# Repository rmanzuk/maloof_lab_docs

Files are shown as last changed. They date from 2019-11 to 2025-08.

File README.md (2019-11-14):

# Lab Recipes

This repo stores and records the workflows for lab and field equipment

### Photogrammetry
- recipe for MicaSense RedEdge MX that formats the data for FRS161 2019.

### GIRI

### Sercon
- data reduction script for Sercon dataset
- workflow for running samples on the Sercon

### GPS
- Trimble differential correction workflow

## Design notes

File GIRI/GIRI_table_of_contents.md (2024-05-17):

# Master markdown file for GIRI
 GIRI is a bit of a Frankenstein machine with a lot of loosely kept knowledge of keeping it running.  This document is an attempt at putting it all together, including links to external files and webpages. From this table of contents, click on the section you want to read about. Sub-documents include helful links, images, and files.

- - -
## Physical Setup / Maintinence
### [Mitsui CNC surface grinder](sub_markdowns/surface_grinder.md)
### [Pneumatic peripherals](sub_markdowns/pneumatics.md)
### [Camera and lenses](sub_markdowns/camera_lenses.md)
### [Wiring / electronics with PLC](sub_markdowns/wiring_plc.md)
### [Summary of products to keep GIRI going](sub_markdowns/shopping_list.md)
- - -
## Operation code
### [MATLAB](sub_markdowns/matlab_doc.md)
### [Connected components ladder logic](sub_markdowns/ladder_logic.md)
### [C++ Capture One SDK](sub_markdowns/capture_one_sdk.md)
### [Other software](sub_markdowns/other_software.md)
- - -
## Data storage and organization
### [giristore](sub_markdowns/giristore.md)
- - -
## Operating recipes
### [Wheel balancing and truing](sub_markdowns/wheel_balancing_truing.md)
### [Dressing the chuck](sub_markdowns/chuck_dressing.md)
### [Focusing the camera](sub_markdowns/focusing_camera.md)
### [Preparing a sample for serial grinding and imaging](sub_markdowns/sample_prep.md)
### [Mounting a new sample for serial grinding and imaging](sub_markdowns/starting_sample.md)
### [Daily operations to grind and image a sample](sub_markdowns/daily_operations.md)
### [Accessing data on giristore](sub_markdowns/accessing_data.md)
- - -
## Education
### [Checklist of things to learn/know for operation](sub_markdowns/education_checklist.md)
### [Known current issues or improvements we would like to make](sub_markdowns/issues_improvements.md)
### [Troubleshooting common problems](sub_markdowns/how_to_fix_problems.md)

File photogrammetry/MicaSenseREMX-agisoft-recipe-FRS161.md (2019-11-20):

# Agisoft Metashape Workflow for MicaSense RedEdge MX---Specifically for FRS161
Bolton Howes, November 2019

**note: This workflow is modified from [this ](https://agisoft.freshdesk.com/support/solutions/articles/31000148780-micasense-rededge-mx-processing-workflow-including-reflectance-calibration-in-agisoft-metashape-pro<strong), to make DEMs and Orthomosaics from MicaSense RedEdge MX photographs**

<!---Press control+shift+m to view in markdown-preview in atom-->

## 1. Add Photos (5 minutes)
- open Workflow menu and choose Add Photos. Select all images including reflectance calibration images and click OK. Select the "Multi-camera system" option.

## 2. Locate reflectance panels
- open Tools Menu and choose Calibrate Reflectance. Press "Locate Panels" button.
- Images with the panel will be moved to another folder and the masks will be placed over the images. If the images are not automatically, see Appendix A from [this workflow](https://agisoft.freshdesk.com/support/solutions/articles/31000148780-micasense-rededge-mx-processing-workflow-including-reflectance-calibration-in-agisoft-metashape-pro<strong). You may need to load a CSV with the calibration information.

## 3. Run reflectance calibration (2 minutes)
- Check on "use reflectance panels" and "use sun sensor" option sin the Calibrate Reflectance dialog to perform calibration. Click OK to start the calibration.

## 4. Enter Ground Control Points (GCPs)
- click on the 'Reference' panel, which is in the bottom left of the Metashape window.
- Right click in the Markers on the left middle panel, and select 'Add Marker'
- Input the differentially corrected Lat/Long/Elev/Uncertainty
- Then right click on the marker you just created and select 'Filter Photos by Markers'
- In the 'Photos' panel only the images with your marker will be present. Double click on one of the images, then drag the predicted marker position to the actual position. Do this on at least 10 of the photos, more if you are feeling ambitious.
- Repeat for all of your GCPS

## 5. Convert from Lat Long to UTM
- In the Refernce panel, the fourth icon from the left is the 'Convert' button. Hover the mouse over it to make sure, then click it.
- The camera is in WGS 84 Lat Long, to convert to UTM, click on the drop down with WGS 84, then select 'more options'.
- Find the appropriate UTM Zone, for example the UTM for Mesoraca, Italy is 33S. So after selection the drop down window would say "WGS 84/UTM zone 33S (EPSG::32733)"
- Make sure both 'Cameras' and 'Markers' are checked on
- press OK

## 6. Align Photos (>5 hours for 1,000 photos. Depends somewhat on GCPs)
- Workflow --> Align Photos
- Use Accuracy: High
- Generic preselection and Reference preselection are checked on.
- Key point limit: 40,000
- Tie point limit: 4,000
- Adaptive camera model fitting OFF

## 7. Optimize Cameras (10 minutes per iteration. ~1-2 hours)
- It is easy to overdo this step. So be careful and keep an eye on the dense cloud to make sure no weird shapes start popping out.
- Go to **Tools**-->**Gradual Selection** and select **reprojection error**. Select all points above 0.5 and press **OK**.
- On your keyboard press delete (FN+Delete on Macs, Del on PC).
- Then press optimize Cameras
- repeat for 2-3 iterations.
- Then using one of the selection tools, select the tie points that that seem bad (i.e. are way above or below the rest of the model) and delete them, then re-optimize the cameras. 

## 8. Build Dense Cloud (Time: 4hrs for 1,000 photos)
The Dense Point Cloud allows us to reconstruct a more accurate DEM.
- Workflow --> Build Dense Cloud
- Quality: Ultra High
- Depth Filtering: Agressive
- Calculate point colors checked on.

**Note: if you do not use Ultra High setting, your DEM will be downsampled and at MUCH lower resolution than the orthomosaic. for example, Medium produces a 1/4 resolution DEM compared to the orthomosaic.**

## 9. Build DEM (Time: 5 min)
- Workflow --> Build DEM
- Make sure the geographic projection is correct. Should be the same as Step 5
- Set interpolation to Extrapolated
- Press Ok

## 10. Build Orthomosaic (Time: 3 hrs)
- Workflow --> Build Orthomosaic
- Default settings
**Note: the Metashape estimate will say something like 12 hours, but it finishes much faster than that**

## 11. Exporting
- right-click on DEM in the 'Workspace', select export DEM
- Choose 'Export TIFF/BIL/XYZ'
- Leave the defaults, except only select 'Write BigTIFF file' in the 'Compression' panel.
- Repeat steps with Orthomosaic

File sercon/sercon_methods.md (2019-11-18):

# Sample Prep for Analysis on the Sercon

## 1. Cut   

  Before you begin, determine which machine is best suited to your sample. The **tile saw** is used to cut fresh surfaces in hand samples. Anything larger can be cut using the **oil saw**. If your sample is porous, consider the implications of filling pore spaces with oil (which will have some Carbon signature) before using the oil saw. Wear safety glasses and ear protection for this procedure.

  ### Tile Saw

  a. Turn on the water using the yellow lever to the back-right of the saw. Ensure there is a light stream of water running over the blade before turning on the saw. **The saw floods very easily** so leave the water on for as short a time as possible.

  b. Place sample on the cutting table flattest side down. Recall that you're hoping to cut a sample thick enough to drill without breaking into fragments under pressure.

  c. With the sample not touching the blade, turn on the saw using the black switch.

  d. Slowly slide the sample through the blade, making two parallel cuts. Note that the blade is diamond tipped, meaning it will not cut your finger if you touch it, but it will cut through your nail.   

  e. Turn off the blade and the water between samples, and remove any sample fragments from the cutting table.

  #### Common Problems
  The hose at the back of the metal pan in which the saw sits will occasionally get clogged with fine silt. Use your finger to unclog the inside of the hose.

### Oil Saw

  a. With the saw turned off, and the lever in “return” position, open the top of the saw. Pull the sample stage away from the blade and place your sample on it. Ensure that the sample is tightly secured, flattest side down, and will not move when the saw is running.

  b. Once the sample is tightly secured, close the top of the saw (pull the hinge that props it open towards yourself), put the lever in “cut” position, and press start. The saw can run unattended.

  c. Once you hear that the saw has completely finished its cut, open the top of the saw and remove your sample.

  d.The sawed sample will be coated with oil. Scrub/soak it with warm soapy water to remove all oil residue before proceeding with polishing or drilling.

## 2. Polish  
Polish non-homogenous samples to distinguish between clasts and matrix while drilling

  a. Ensure samples are clearly labeled on multiple sides and that the polishing surface is completely flat. If you need to flatten your sample, use wet/dry sandpaper.

  b. Evenly spread one cup of silicon carbide over the polishing tray, and pour a thin layer of water over it.

  c. Turn on the polisher using the black switch (hanging) by the bucket of rock waste. Silicon carbide water splashes out, so don't stand too close.

  d. Draw a black line across the sample using a Sharpie, and place the samples line-side down on the polishing tray.

  e. Turn on, checking periodically, and adding silicon carbide and water as necessary. Samples are polished when the black line is gone.

  g. Clean and dry the polisher. Using paper towels, remove and dry the rubber ring in the polisher. Absorb most of the liquid remaining on the polishing table using a sponge. Hose dry any remaining liquid (using the extendable air hose over the work table). Improper drying will rust the polisher.

## 3. Drill
  Used to produce powders for running on the Sercon for C and O isotopes. Wear safety glasses for this procedure.

  a. Ensure the drill is clean and has the right-sized drill bit. The chuck is latched on the top left of the drill, and it can be used to change the drill bit.  

  b. If necessary, adjust the stage by unlocking the red turn key on the left of the drill and turning the crank on the right. Lock the turn key after adjustment.

  c. Place sample on the stage, ensuring the flat side is flush to the stage surface. If the sample is not flat, place it on red bean bags for support. Always ensure that sloping rock surfaces are sloping away from you to avoid injury.

  c. Drill a shallow hole in sample (< 1-2mm). The best places to drill are often the most homogenous areas of the sample. Note that this can vary from project to project - it may be necessary to sample from clasts, fossils, or other heterogeneities. Multiple drill holes may be required to obtain enough powder for analyses.  

  d. Ensure plastic sample vials are clearly labeled on cap and side, and use weighing paper to transfer powder into vials.

  e. Use the air hose to clean the drill bit, and drilling surface in between every sample.

  #### Common Problems

  The head of a used drill bit might break if too much pressure is applied. When this happens, the head flies off, downslope. Always ensure that sloping rock surfaces are sloping away from you.

## 4. Weighing samples
During this step, you will weigh out samples for sercon analysis. **Note that procedures for standards are highly subject to change.**

a. Locate clean sample vials on the lower shelf of the oven. Bring vials to your weighing space (to the right of drill).

b. Air hose the table and wipe down the surface with kim wipes.

c. Determine the layout of your standards and samples by following the diagram below, and clearly label the vials as such. Samples will occupy the blank spaces. Run order is right to left from the bottom to top most row.

| N 	|   	|   	|   	|   	|   	| V 	|   	|   	|   	|     	|     	|
|:-:	|:-:	|:-:	|:-:	|:-:	|:-:	|:-:	|:-:	|:-:	|:-:	|:---:	|:---:	|
| V 	|   	|   	|   	|   	|   	| V 	|   	|   	|   	|     	|     	|
| N 	|   	|   	|   	|   	|   	| V 	|   	|   	|   	|     	|     	|
| N 	|   	|   	|   	|   	|   	| V 	|   	|   	|   	|     	|     	|
| V 	|   	|   	|   	|   	|   	| V 	|   	|   	|   	|     	|     	|
| N 	|   	|   	|   	|   	|   	| V 	|   	|   	| V 	| CMT 	| CMT 	|

d. For the NBS standard, weigh out 15–20 grains using the metal scooping tool. This is a scoop and look technique, and it is quite approximate.  

e. For the VTS standard, use the black well to weigh out two (tightly packed) to three (loosely packed) "divots". If it is your first time using the VTS standard, weigh out three divots.

f. Place the well over the vial with the divot side facing down. Tap the top of the well to ensure all of the powder enters the vial.

g. For the CMT standard, weigh out one divot. Repeat step f.  

e. When weighing samples, use the black well to weigh out one to three divots. The necessary amount of powder for each sample is dependent on its carbonate content, as well as the sensitivity of the machine. Most samples require two divots, unless a test run shows otherwise.

f. Allow rack of vials to sit in oven for at least an hour to remove any moisture from the samples.

# Mass Spectrometer Analysis - Starting and Monitoring a Run

## 1. Load Acid
Wear gloves for this procedure

a. Under the hood, unwrap the para-film sealing the acid container.

b.Using a small plastic funnel, slowly pour acid into a small glass vial, filling it to the top.  

c. Cap the vial and place it in the heating block in the columns to the far right.   

## 2. Flush
a.	Remove the rack of vials from the oven. Partially screw on the caps for all tubes, using different colored caps for standards and samples. Caps should be screwed on just enough so you can pick up the vial using only the cap. It is good practice to randomly cap vials to eliminate potential for systematic isotope fractionation due to exposure to moisture in the air.

b.	Systematically go through and tighten each cap. When tightening the caps, tighten until you notice a divot forming in the septum. Then, loosen slightly until there is no divot.

c. At the He flush station, insert loose needles into the edge of the septa. Avoid puncturing the middle. Discard any bent/broken needles in the red sharps box by the flush station.

d. Insert flush needles into horizontal vials, starting at the pressure gauge, and ensuring that the flush needles only puncture the edge of the septa. The flush needles are connected in a series-circuit style. This means they should always be added to the system in sequential order (starting at the first needle) and be removed in reverse order. Following a different order could contaminate the vials with atmospheric air.

e. Any flush needles that aren’t puncturing vials should be capped with gray, circular rubber stoppers.

f. Turn on He (taller tank to the right) in the closet, using the left most knob on the regulator, and the knob on the tank. Turn pressure gauge on flush needles to approximately 80 psi.

g. Flush vials for about 8 min.

h. Leaving the He on until all vials are removed, remove vials in reverse succession.  

i. Once all the vials have been removed, turn off the He pressure gauge only - a full run requires two rounds of He flushing. The pressure gauge for the He flush needles should be turned off while putting on the next set of vials, however, the He tank can remain on during that time. If you are doing a smaller run, you may skip this step.

j. After all the vials in the run have been He flushed and disconnected from the He flush needles, the pressure gauge should be turned to 0 and both knobs on He tank should be closed.

k. Remove all loose needles from the vials before loading samples into the heating block.

## 2. Loading Samples
a.	Open Callisto1055 program.

b. Click Sample List in upper left corner, and the previous sample list will pop up.

c.	Rewrite sample list with new sample names. The program does not support decimal points, and so may suggest reviewing errors in the list, if you accept errors, it will automatically correct decimal points to underscores.The last two columns should read: Weight = 100, Set Up = CTC-8. The last row should have the sample name “END”, Weight = 0, and Set Up should be empty.

d.	Save As a new file with the format mmddyy_ABC (ABC = your initials).

e.	Load vials row by row into heating block in same order as entered into the sample list. Keep the lid on the heating block as much as possible while loading since heat is lost very quickly.

f.	Allow heating block temperature to equilibrate to 69–71°C, to avoid fractionation of oxygen isotopes during acidification. This temperature can be reached faster by insulating the heating block with foil.

## 3. Acidification
Use gloves when completing this procedure.

a. Remove two small needles from the bag of small blue needles, and a syringe from the box in the right most, under bench storage closet. Tighten the needle on the syringe to avoid leaks.

b. Prior to acidifying, use a small blue needle to puncture the edge of the septa of each vial to release pressure.

c. Remove the acid vial from the heating block after the acid has heated for at least 1-2 hours.

d.	Insert small needle into the edge of the septum on the acid vial to allow for air to flow in as acid is drawn.

e. Puncture the other edge of the septum with syringe. Holding the vial upside down, draw in acid. A full run (72 vials) needs close to two full syringes for acidification.

f.After drawing acid, return the acid vial to the block, to keep it warm (and less viscous).

g. Holding the syringe needle vertically, with a kimwipe wrapped around the top, slowly press the plunger to remove any bubbles. If bubbles remain behind, pull back the plunger to create an air pocket, and then repeat the process until no bubbles remain (in the syringe or in the green neck of the needle).

h. Starting at beginning of run, puncture the bottom left corner of the septa (see figure below), inserting enough acid to react with the sample completely. This is generally about 3 drops or half the distance between the markings on they syringe. Angle the needle towards the vial wall so that the acid flows down the side of the vial. This is crucial so that the acid warms up as it drips down the side, and reacts properly with sample. Keep count of the acidified vials.

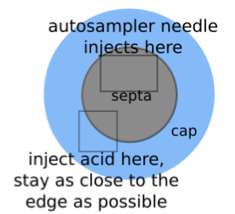
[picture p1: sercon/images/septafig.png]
septa figure


i. If there are any visible drops of acid on the septum, wipe them off with a q-tip before starting the run.

j. Start the run 1.5-2 hours after the first sample was acidified. This allows for most of the samples to dissolve completely.

#### Mixing Acid
Follow this procedure when there are multiple vials of acid in the heating block or we are running low on acid.

a. Once there are a few vials of used acid in the block, empty them into the acid container.

b. Place container on the hot plate in the hood at 150˚. Cover with a watchglass and stir with stirring rod until the mixture looks homogenous, then let it cool to room temperature.

c. Pour acid into a plastic measuring cylinder and use the hydrometer (in drawer labeled foil/tape) to measure the density. If the density is between 1.9 and 1.95, pour the acid into the container, and seal it. If not, add a small amount of phosphorous pentoxide, mix until dissolved, then cool and re-measure density.

d. When acid runs out, follow instructions taped to the hood to make a new batch of acid – wear gloves, and a lab coat while dealing with phosphoric acid and phosphorous pentoxide. Always start with ~50% phosphoric acid volumetrically, since phosphorous pentoxide will increase total volume i.e. for 100 ml of acid, start with ~50ml of  phosphoric acid.

## 4. Starting the Sercon

a. Wipe the sampling needle clean with a kimwipe. Change out the septa in the He flush valve on the left side (new septa can be found in the drawer just below the keyboard).

b. Record He, and Ref1 values from the gas bench in the lab book.

c.	Record the vacuum reading from the program (as a fraction A/S), and the reading on the He tank on the right wall of the closet.

d.	In the source control window on the right, click Load, then select “CO2.src”

e.	Turn on CO2 by clicking the CO2 tank on the mass spec diagram and wait for the mass 44, 45, and 46 (colored bars) to stabilize. Record those values.

f.	Click “peak 2”, and then “center” once the graph appears. This checks whether the magnet is centered. If the magnet is centered, there will be a green line at the center of the curve. If not, two lines, a red and a green, will appear. The green line is the center. Click “Enable” on the source control window, and use the right most single arrows to move the red line. A black line appears to show the direction in which the line is moving. Re-center if needed and save (rewrite) CO2.src if the HT value was changed. If the value was changed, re-check the center after saving the file.

g. Record HT, HP, Focus, Trap, eV, IR from the source control window.

h.	Close CO2 by clicking button on diagram again.

i.	Click “Start” (top left), and make sure it has the correct sample list name (mmddyy_ABC). Okay the file name, then source file, tick the box for stand-by, and okay the last window.

j.	The run will start, and graphs will appear in the middle window. Click “Toolbar” then “Set axes”, click save and exit, and then “Redraw” to properly scale the peaks.

k.	The first five peaks (square) are reference peaks. Record “load” and “inject” values from the flowmeter for the first non-reference (curved peak) at the start of the run.

l.	Compare all values recorded in the lab notebook to previous values. Notify the appropriate person if you notice a difference in these values.

m.	Periodically record tuning parameters in “Sercon tuning log” Excel spreadsheet on the Mac by the scopes.

## 5. Monitoring run

a. Ensure that at least the first two curved peaks look normal

b. Check sercon periodically, but it can be left alone overnight.

c. After the run has been completed, change out the septa in the He flush valve on the left side (new septa can be found in the drawer below the keyboard). Make sure the septa isn’t screwed on too tight (the septa should not be convex).

# Mass Spectrometer Analysis - Data Reduction

a. Open the Reprocessor and use the “Replay” button to find and open your file. If the Reprocessor was open, your file will not appear the first time you hit “Replay”. You will need to close the Replay window and reopen it to find your file.

b.	Go through the non-reference (curved) peaks for all samples and check that they are approximately the size of the reference peaks. Any peaks that are too low might correspond with popped caps, broken vials or undissolved sample. Peaks that are too high or too low will likely yield data with high standard deviations, and may need to be re-run.

c. Leave vials in heating block while reducing data to corroborate any anomalous values with vial order, popped caps, broken vials, etc.

d. The Sercon computer is not connected to the Internet. Save the “mmddyy_ABC.prn” file for the run onto a flash drive. The file can be found in a folder within the “Replay shortcut” folder on the desktop.

e. All data reduction is done on the Mac by the scopes. Drag and drop the .prn file into the “Raw Data” folder in Matlab.

f. Switch to the “Original_Sercon_Code” folder. Run the script “sercon.m” using the following command: sercon('mmddyy_ABC.prn',a,b) where mmddyy_ABC is the filename, a is the number of samples in the run, and b is the desired starting sample (almost always 1).

g.	A 5-subplot figure will be presented. The histogram in the lower left corner illustrates the occurrence of peak areas for each sample/standard. The peak area is the amount of gas collected for that measurement. The scatter plots (subplots 1-4) show peak area vs. raw ratio of carbon and oxygen isotopes for the standards.

h.	Select the peaks to include in the reduction. As the isotopic ratio for each peak is partly dependent on peak area, it is important to exclude any peaks that are too small or too large, since including them could produce large standard deviations.

i.	Click on the histogram to select the peak areas that will be used for data reduction, starting with the lower-bound (left) and ending with the upper-bound (right). This will need to be done twice, once for carbon isotopes and once for oxygen. It is best to exclude the tail ends of the sample peak area distribution. Ideally, there will be a Gaussian distribution of peak sizes.

j. A new 4-subplot figure will appear. The top two plots illustrate the raw carbon and oxygen values of each peak of each NBS standard, while the bottom two depict the same for the VTS standards.

k. Matlab will give the prompt “Exclude any NBS?”
Exclude any NBS standard that does not fit a line of best fit with the other standards, either with regard to carbon or oxygen isotopes.  

l. Matlab will then give the prompt “Exclude any VTS?” Repeat step k for VTS.

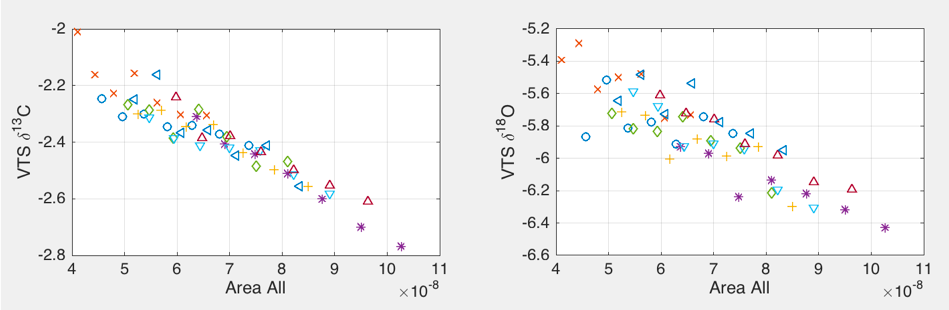
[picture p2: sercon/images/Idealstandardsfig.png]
ideal standards figure

Ideal configuration of standards, where all standards follow a tight, linearly decreasing trend  

not standards figure
Highly variable standards, which indicate a problem with the sercon or sample loading

#### Common Problems - Steps j-l

a. The machine is tuned to optimize accuracy over a certain range of peak sizes. If the peak area is way too small or way too large relative to the reference peaks, it can be out of range for how the machine is tuned and won’t produce accurate data. If the sample just prior to a standard has a peak size that is way too large, it can overload the collector and influence the results.

b. If the sample was not acidified completely or acidified at the incorrect temperature, it might have fractionated away from the standard’s reported value.

c. If a cap pops off, the seal is broken and atmospheric air flows in. The CO2 gas produced from the reaction of acid and sample may leak out and the machine then measures air. Because air has much less carbon than CaCO3, the peak size will be extremely small. This is probably the most common error.

d. If the needle or tubing is clogged with septa or acid then not all of the gas will reach the collector.

e. If a flush needle is leaking, then atmospheric air will still be in your vial and it won’t have completely flushed with He, meaning it will slightly change the overall measurement.

ideal peaks figure
Proper sized sample peaks

## Data Reduction Continued

m. 4 new figures will pop up. They are stacked, so move the figures apart to see all of them. Figure 1 shows all of the standards included in the reduction. Use this graph to answer the prompt: “Which is the primary standard?” This will be the standard that the data is corrected to in the case of a single point correction. Use the standard with the most data points as the primary standard, as it will be more statistically robust.

n. Figure 2 shows those standards if they were to be adjusted using the linearity defined by the NBS standard slope. Essentially, Matlab is determining the slope of the line of best fit through the NBS data and rotating it to horizontal. It then translates this line up or down to pin it to the known value of the standard, and then makes this correction for all NBS data (top two graphs) and all VTS data (bottom two graphs). This is a way to correct our data so that the isotope values are no longer biased towards peak area. Figure 3 shows the same thing but using the VTS slope. Figure 4 uses a slope that is the average of the NBS and VTS slope.  

o. Determine which slope best represents your data. The slope correction that minimizes standard deviations for carbon and oxygen will be the most accurate correction. Sigma values should be 0.1 or lower for carbon and 0.25 or lower for oxygen.

p. Matlab will give the prompt: “Which slope should we use?” Enter N, V, or mu (mu = μ = average) depending on which slope is most accurate to reduce data with.

q. You will be presented with a final figure containing two subplots. The knick point in each plot (y = 0) is the known value for the primary standard.

r.	Use the graph to estimate the difference between TP and SP for the secondary standard. Do this by first locating the value of your secondary standard on the x axis. Then, see where this x value intersects the plot. Ideally, the y value (difference) should be < 0.1 for d13C and < 0.25 for d18O, which indicates that the standards are in agreement. In this scenario, it is best to reduce the data using a TP correction. If the difference is much greater than this range, it is best to make a SP correction. Enter TP or SP for prompt “Two-point or Single-point correction?”

Note: If you are unsure about which correction to use, try reducing the data twice, once with each type of correction. Use whichever method produces the most consistent standard values, or rerun if neither creates reliable standards.

s. Final dataset will be produced. Several files recording all of the selections you made are saved. Open and examine the file "reduced_mmddyy_ABC.csv" in excel (open outside MATLAB).

t. Standards are expected to have the following values:

VTS: -1.48 ± 0.1 for d13C and -8.54 ± 0.25 for d18O

NBS: 1.95 ± 0.1 for d13C and -2.20  ± 0.25 for d18O

u.	Investigate any anomalous data points, by cross-referencing peak shape/size on the Reprocessor software. Consider rerunning samples if standards do not fit constraints or if there appears to be drift in standard values throughout the course of the run.

v.	Record standard values and data reduction parameters in “Standards” Excel spreadsheet.

# Common Problems

## Popped cap
Some of the vials have faulty threads that are incompatible with the caps, which can lead to caps “popping off” in the heating block as the plastic heats up and expands.

#### Symptoms:
This is easily identified using the Callisto Reprocessor software. The peaks for these samples will be completely flat lined, except for perhaps a small first peak.

popped cap figure
Diagnostic peak shape of a popped cap

#### Solution:
Identify vial in heating block and check to see if cap is crooked or loosely sitting on the vial. Remove the vial, wash out the acid with DI and put the vial in the broken glass box by the sink. Sometimes, the caps may be faulty. In that case, use those caps for acid vials and not for samples or standards.

Samples without any carbonate content or caps that are not screwed on completely can also give the same diagnostic signal in Callisto Reprocessor. Ensure this is not the case before throwing out a good vial.

## Clogs

Clogs can cause a spectrum of problems for the Sercon. Minor clogs, caused by pieces of septa or a thin meniscus of acid blocking part of the needle, are usually resolved on their own when the acid is pushed through to the trap. Clogs in the needle can be easily cleaned out. Acid clogs can create serious issues for the Sercon if they make it to the gas bench. This requires a lot a work to locate and clean out the acid, which blocks gas flow and corrodes parts of the machine.

#### Symptoms:
Clogs create variable data, as isotopic fractionation occurs when CO2 is not allowed to flow freely through the capillaries. Clogs are identified by irregular peak sizes and sporadic measurements from the flow meter. Take care to inject vials properly during acidification; improper acidification technique is the leading cause of clogs.

clog peak figure
Irregular peak size indicative of a clog

clog figure
Chronic clogs can also be identified during the data reduction process. Figure depicts distinct groupings of standards, which also show a gradual increase in value over the course of the run.
#### Solutions:

Contact the Lab Manager

## Unmixed acid

Always acidify using a vial of fresh acid. Combining the remaining acid from previous vials without proper heating and mixing can create variable data (see figure below).

unmixed acid figure
Highly variable standards coincident with recycling remaining acid from previous runs

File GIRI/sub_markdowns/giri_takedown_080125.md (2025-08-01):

## First, we removed the camera and its wiring. 
1. Remove camera curtain, which is velcro-ed on top around camera housing. 
2. Remove ethernet, which is a blue cord wired though the top of the camera housing. 
3. Remove the camera back: Push button on RH side, pull up to get the back out. Black square plate goes on the top of the non-viewer side. Remove batteries and put them into the appropriate slit in the foam in the large black case. We packed this into the black zippered case and into the large black box, inside the foam. The 72 mm lens, back, and batteries are all inside the white foam piece.
4. Loosen the yellow levers on the front (facing you) of the grinder to lower the ringlight. The use Allen keys (red and yellow cases) to remove the camera itself. It was set in the track, rotated so that the notches matched. The two screws are on the LH, RH sides of where the camera sits. Pictures 3908 and 9000 on PMH phone.
5. We packaged the IQ4, 72mm lens, 120 mm lens, and charger in the black box thus labeled. 

## Next, we removed the light bricks and ring light.
1. Lights 7, 8 (7 is the one closest to you when facing grinder) are the yellow cords that we unscrewed from these bricks. Pictures ...1455 and ...8445 on PMH phone. 
2. Use Allen key to remove the UV bricks by the silver arms. We taped the 2 screws along the top rim into place.
3. Took wood glass filter out (pop out 3d printed side guard, slide out) and cleaned with lens wipe. Both filters are in the same box. 
4. Unscrew ring light cords, which are labeled as L, R when you are facing grinder. Picture ..1592 on PMH phone. At this point, all cords to camera and lights are disconnected.
5. Use Allen key to unscrew ring light's connector on the right (when facing grinder). There are 3 screws; we did the closest one first. Hold up the ringlight while unscrewing. Picture ...3612 on PMH phone.

We left the rest of the camera apparatus on the grinder. 

## We then removed the roller and other connected devices.
1. On the grinder console, Func. 1 and OUT1 to move roller up and down. IMG_8892 on ACM phone. 
2. When it is up, unscrew rightmost screw on yellow 3d printed piece using Allen key, then slide off blue piece laying on top of the rim. 
3. The oil coolant unit (autolubricator) is the b/w box on the RH side of grinder. Fill it with oil from the red oil container near the coolant box. Picture 2577 on PMH phone. 

Note: The extra active wheel is 320 grit. The one currently on grinder is 400 grit. 

## PLC takedown. 
1. Grinder connection is thick yellow cord. Goes into RH side of PLC when facing PLC front. 
2. Disconnected the air--took off its yellow cord, which is in the back right when facing PLC front. 
3. Turn off grinder by flipping switch on front of grinder. 
4. Unplug black cord, which is power for the PLC.
5. Unplug gray/white PLC data to computer cord. 

## Coolant tank. 
1. Take off covers and top. 
2. Screw out the filter (hoses in front). 
3. Clean out tank and replace filter paper as needed.

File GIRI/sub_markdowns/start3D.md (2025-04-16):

### For 3D grinding + imaging
*If you are not already comfortable with positioning the grinder for ```rasterflat``` and/or setting positions and working in grinder coordinates, I suggest you practice rasterflat **first** (this will be useful for getting your sample ready to grind, anyway...)*  

Make sure the camera is on and the lens cap is off. Check coolant levels (>6") and refill. LOAD a previously used grinding code. For example, `20250416.JKW.G001.focus` adapts the old code to move the sample into the focal plane before taking images (and out of the focal plane when the imaging is done). If the camera focus is not at the bottom of the wheel, use a .focus script).  

Before grinding, we need to set X0, Y0, and Z0 (in relative coordinates). 

Z0 should be -1.00000 in MACH coordinates. This is our imaging position.  
Y0 should be at the highest point of the sample, find this carefully!  
X0 should be at the edge of the rock closest to you. The table will move *out* towards you in X as it grinds.  

In the GCODE, also set the X depth like in rasterflat.  

LTEACH and RTEACH tell the table how far to move in Z. Set these to the outer Z limits of your sample, with some (~0.5-1") room to spare.  

Enter the number of loops (L) in the usual place at the top of the code.  

Before engaging the magnet, make sure your sample is nicely centered under the lens **when the table is at Zmach = -1.00000**. Check this by opening live view in captureOne and turning on a light in matlab (serial_command('LIGHTS_000010000') turns on green). **The camera is fixed in X, so do not worry about the X position.** The only X pos in the code is where you want the grinding to start on the sample (edge closest to you).  

Once all the positions are set to 0 as detailed above, START the program, then go to the computer and, in Matlab, run ```barebones_serial```. If you have not already, create a New Session (cmd+N) in CaptureOne in the /GIRI/Data/ directory. When barebones_serial asks "which folder are the ... found in", select this newly-made folder. When barebones_serial asks how many grinds to expect, enter the number of loops you saved in your code.

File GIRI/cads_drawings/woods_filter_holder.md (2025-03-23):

# Placeholder

Asked Dave for Wood's glass filter frame design on 3/23/25.

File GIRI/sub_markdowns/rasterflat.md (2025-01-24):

# A COMPLETE GUIDE TO FLATTENING SAMPLES
## 0. Preparing your samples.
Are your samples...  
- [ ] Glued?
- [ ] Documented in the notebook?  
    page: ____  
- [ ] Photographed on the Nikon?    
    photo number: ______  
- [ ] Polished on in the lapidary so that they are mostly flat?

**If all four of these steps are complete, you are ready to get the grinder set up.**

## 1. Pre-grinding preparation.
**Polish**  
- [ ] Polish steel plates:
    - Apply a drop of **sharpening stone oil** (white cap) to the steel.
    - Using the **red stone**, polish in a figure 8 pattern until the stone passes smoothly over the steel.
    - Apply a few drops of 3-in-1 oil to the steel. 
    - Finish polishing with 10 figure-8s of the gray stone.
- [ ] Polish the chuck with the tan stone and 3-in-1 oil. Leave oil on the chuck.
**Check oil and coolant levels**  
- [ ] Check coolant levels. If less than 6", mix more coolant (see section 1.a. below.)
    -[ ] (Add coolant if needed)
- [ ] Expose new filter paper (on the roll)
- [ ] Check the back of the machine to see if leaked oil is close to filling up the overflow tub.  
    - If it is, pour waste oil into the waste container  
- [ ] Check lubricant levels on the front of the grinder. Refill with **Mobil Vactra** (blue container, in the cabinet).
**Turn the grinder/wheel on**
- [ ] Put safety glasses on (look around all 3 rooms in the lab if you cannot find any)
- [ ] Turn on the wheel (button on the computer screen) and let it run for 10 minutes if it has not run yet today.
- [ ] Turn on the coolant (button on the computer screen)
- [ ] Use the pipette to take up some coolant and make a refractrometry reading. Record this in the grinder notebook.
- [ ] Turn off the coolant.
- [ ] Turn off the wheel if it has been on for more than 10 minutes. (Fine to leave it on, too, it just might get in the way.)
      
**Sample placement**  
When flattening, you are trying to minimize time spent flattening while maximizing the number of samples that are flattened to the same heigh. So, select bars with samples that are already very close to the same height. If you don't have any, that's ok, you can flatten (and image) one bar at a time. Better to do that than spend hours needlessly grinding some bars way more than they have to be to get flat.   
Note: One of the UV brick lights gets in the way of the table, so the table **can only move so far in the Z (horizontal L/R) direction!!**  
**Z-limits (in MACH coordinates): 0.5" to 13"!**  
- [ ] Put a little 3-in-1 oil on bars and grinder chuck. 
- [ ] Place bars on chuck **ensuring that the table will not hit the UV light!!**
- [ ] Engage magnet.
You are now ready to set up your grind.

## 2. Setting up a rasterflat run.
We will always *raster* flatten our samples. It is better for the wheel and leads to a nicer finish. This means we take make one pass over the whole grinding area, then move the table up one step and do it all again. It takes a while, which is why it is imperative that your samples are mostly flat and mostly the same height before you begin.  

#### A. Measure your grinding area.  
FIRST: Move the table in the Y direction (vertical) so that there is at least an inch of space between the bottom of the wheel and your tallest sample. This ensures you do not accidentally damage the wheel.  

##### i. R and L TEACH
As the rasterflat code proceeds, the grinder will move the table in the Z direction (north-south) between two points called **L TEACH** and **R TEACH**. As the name implies, we have to "teach" these positions to the computer. Do this by moving the table so that the wheel is over the farthest left (north) edge of your samples + 0.5". At its maximum extent, this should be Z=0.5 in MACH (machine) coordinates. Press **L TEACH** on the right side of the control computer screen.   

Now, move the table so that the farthest right (south) side of your samples has cleared the wheel. At its maximum extent, this should be Z=13 in MACH coordinates. Press **R TEACH**.

To test, you can **START** the table. The table should move back and forth between the L TEACH and R TEACH points you set. Stop the table.  
##### ii. X dimension
Next, we have to figure out how wide the grinding area is (X direction or east-west). We will record this parameter in the G-code as ```X```. To do this:
1. Move the table in X so that the wheel is closer to you than all of your samples, with only a half-wheel overlap of the closest sample. (furthest west). Write down the X position in MACH coordinates:  
X0 = ____  
2. "Zero" the position so that we can come back to this X position later. (Press POS, ALL, 0 SET). All REL positions should now be zero.
3. Move the table so that the wheel is farther away from you (+half-wheel thickness) than all of your samples. Again, record the X position in MACH coordinates:  
X1 = ____  
4. The difference between X1 and X0 is the ```X``` value we will record in the G-code line that reads:
   ```G91G01X6.5F150```
You can go ahead and edit that line now to whatever you calculated. Round to one decimal point.

##### iii. Y start
You want the grind to start as close as possible to the tallest part of your sample. So, move the table well away from the wheel and lay a ruler or other flat object on top of your samples to figure out where that spot is. Once you have a since for the tallest region:  
1. Turn the wheel and coolant on (press the buttons on the control computer screen) and make sure you are wearing safety glasses.
2. Move the table so that the tallest area of your samples is close to underneath the wheel.
3. Move the table up (Y dial) *sloooowwwwlllyyyy* just until you hear the wheel barely graze the top of your sample. You should use the ```x1``` movement increment (0.0001") when you get close to the wheel.
4. Back off one or two clicks.
5. To check that you really did find the tallest spot, slowly move the table around in the horizontal (X-Z) plane to make sure the wheel doesn't touch anywhere else. If you were right, great. If not, re-calibrate with whatever new tallest area you found. Moving slowly ensures you do not damage the wheel.  

At this point, the Y position (in all coordinates) should be close to where we want to start the grind. However, ```rasterflat``` *starts* by raising the table 0.001". To account for this, we should start with Y backed-off at least 0.001" from the tallest point you found.  

6. Switch to the ```x10``` movement increment (0.001") and move Y 1 click *more positive** (table down). At this point, you will not touch the Y dial again.

##### iv. Move to the starting position
The program does not "get" any positional information from the grinder -- we must start the program from the position we want it to begin grinding at. To accomplish this,   
1. Move the table in X until X = 0.00000 in REL coordinates (you set this point before).
2. Move the table in Z until the Z value is close to your L TEACH value (this is recorded on the computer screen).
3. (Y should not have moved since you set the table height in the step iii!)

#### 2. Record your parameters and edit the G-code.
There are some important parameters that we have to record -- in the grinder notebook and in the grinder's G-code -- before we can begin.
### PARAMETERS.
Fill these out at the start of each "run" (each time you re-start the program rasterflat.txt!) We will document the parameters used for each run in the Grinder Notebook (which lives in the grinder computer room). 

#### Check and adjust these parameters in the G-code:
- ```L##```, where ## is a number (e.g. 50) that tells the grinder how many times to **L**oop (i.e. how many times to raster over the grinding area). **Do not set L>200**. If L is too large, we risk grinding away all of the rock. Let's avoid that.
- ```X#.#```, this is the difference (X1-X0) you calculated in step ii.4.
- ```F###```, the **feed rate** determines how fast the table moves under the wheel. **150** is a good starting point. If the samples are very hard (e.g. they contain a lot of chert or iron), a slower feed rate (100?) might be better. In general, do not change this if it is already set to 150.
- ```Y-0.001```, *just check* that the Y increment is set to -0.001. This is how far we will step the table up (closer to the wheel) each raster.
  
**IF YOU DO NOT KNOW WHERE THESE PARAMETERS EXIST IN THE ```rasterflat``` CODE, CHECK THE EXAMPLE CODE (```20250121.demo.rasterflat.txt```) AND ASK JULIA/ADAM.** Note that you can always demo your code by moving the table in Y so that it is very far away from the wheel and running one loop (L1) to see how the table moves. **But, it is better to just ask questions!!**

After checking/adjusting these four parameters, you can save the G-code file. Do not overwrite the ```20250121.demo.rasterflat.txt``` file. Instead, rename your file in the format:  
```YYYYMMDD.INITIALS.FXXXX.rasterflat.txt```  
```YYYYMMDD```: today's date.  
```INITIALS```: your initials.
```FXXXX```: the "**F**lattening group" you are about to grind flat.  
e.g. If I am going to flatten flattening group 1 (the first set of 2025 flattened bars) today, my code would be called:  
```20250123.JKW.F0001.rasterflat.txt```

#### 3. Start the code
At this point, the table should be in the position you want to start at. the X and Z REL positions should be very close to 0.0000, but REL Y will be some other number. **Reset everything to 0** before you start the run. (POS > ALL > 0 SET).  

If the table is positioned correctly, **the magnet is engaged**, you did everything on the checklist, and you have recorded your L,X,F parameters in the notebook, you are ready to press ```PROGRAM START``` (big green button).  

Stay in the room and monitor the first pass over your samples. If everything went as planned, you can leave. Sometimes it is helpful to time the first loop so that you have a sense for how long the whole run will take.

## 3. Finishing a run.
The code ends on its own and will stop the table, turn off the wheel, and turn off the coolant. So, it's okay if a run ends and you are not around to witness it. When you do come back to retreive your samples, if the samples do not look totally flat yet, restart your code (think about adjusting ```L``` depending on how much more material you want to remove) *without adjusting the final Y position*.   

If your samples are flat, you are done. Just a few more things to do:
- [ ] Record the final Y position (in MACH coordinates) in the grinder notebook. It will be something like -7.5757. (In REL coordinates, it should be 0.001 * the number of loops (L) that you ran.) The final Y MACH will help us focus this batch of samples.
      Y MACH at end: _____
- [ ] Move the table down so that the samples are far away from the wheel.
- [ ] Disengage the magnet
- [ ] Take a picture of each bar using the Nikon camera. Save the photo in the "PostGrind" folder and record the image number in the "PostGrind" .txt file. Place the imaged bars in a tray and make sure the tray is labeled appropriately.
- [ ] Mark each of the samples you flattened as "flattened" on the master spreadsheet.

### TROUBLESHOOTING
**Help! I need to stop my run!**
You can always press PROGRAM STOP to stop the execution of whatever G-code script is running. If things are really bad, you can also hit the emergency stop button (big and red). Stopping the program does not stop the table moving, so you also have to press TABLE STOP. Adjust your code, fix whatever went wrong, and re-start (or ask Adam/Julia!). (It is not bad to stop a run for any reason.)

### A. Sub-routines.
#### 1. Mixing coolant.
If coolant levels are below 6" (use the yellow measuring stick to measure), you need to add more coolant. If levels are just below 6", make one recipe (5L water). If levels are well below 6", make a double recipe (10L water).  
**COOLANT RECIPE**
1) Pour 5L of **DI water** into grey bucket.
2) Pour 125 mL of **Astrogrind** coolant (in cabinet) into plastic measuring cup (on sink).
3) Add the Astrogrind into the bucket of water.
4) Stir with the wooden paddle.
5) Once mixed, add the whole mixture to the coolant tub **through the filter paper**

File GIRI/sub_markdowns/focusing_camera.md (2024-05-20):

## Basic steps for getting camera in focus with the grinding plane

THE CAMERA AND LIGHTS SETUP NOW IS VERY HEAVY AND CAN BE DIFFICULT TO MOVE UP AND DOWN. RECOMMENDED TO HAVE TWO PEOPLE SO AT LEAST ONE PERSON ALWAYS HAS A HAND ON THE CAMERA.

1. **Prepare a sample**: You need a surface to focus on that you know is in-line and parallel with the grinding plane. This can be a piece of paper or a sample that you know is flat. Place a mounted sample in imaging position on the chuck, and then use either sample_flatten or raster_flat to get a flat surface that occupies most of the field of view.

2. **Set up for focusing**: Once your sample is flat, keep the table at the same y-position and move the z-position back to imaging position the field of view of the camera. Go to the control iMac, turn on the green light, and open live view in Capture One.

3. **Set the fine adjustment to middle positoin**: Finer focusing of the camera will be easier if you start in the middle fine adjustment setting and have as much room as possible to move in either direction. Twist the fine adjustment thumbscrew (circled in orange [here](../photos/camera_focus.jpg)) to the approximate middle of its range.

4. **Coarse adjust the camera**: Coarse adjustments are made by using an allen key to loosen the camera mount sled on the camera rail (circled in green [here](../photos/camera_focus.jpg)). ONCE LOOSENED, THE CAMERA WILL DROP IF NOT SUPPORTED, SO HANDS ON THE CAMERA. AGAIN, PREFERABLY A 2 PERSON JOB AT THIS POINT. Because your hands will be moving in and out of the live view feed, you probably cannot use the auto focus tools, so you will have to just move it to a position where it seems roughly in focus by eye. Then tighten the allen key back up.

5. **Fine adjust the camera**: Now that the camera is roughly in focus, you can use the fine adjustment thumbscrew to get the camera in focus. Prior to moving the fine adjustment, set up some focus boxes on the sample surface in the Capture One live view, so you can track focus. Then use the fine adjustment thumbscrew to move the camera (left to lower, right to raise) until you get the sample in optimal focus as judged by the focus boxes. If you cannot get it into optimal focus within the range of the fine adjustment, return the fine adjustment to the approximate middle and repeat the coarse adjustment based upon what you learned from the first attempt.

6. **Check focus on captured image**: Once you think you have the camera in focus, take a picture and check the focus manually. I also tend to capture a stack of images at ~half turn increments of the fine adjustment over the range of a full turn in either direction and select the position associated with the image I deem to have the best focus. This step is a little like subjective splitting hairs, so don't fret too much if you can't tell the difference between two images. You should just leave this step feeling confident the camera is in the best focus you can get it.

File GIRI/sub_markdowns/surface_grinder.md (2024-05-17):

## Mitsui CNC surface grinder

The basis for GIRI is a Mitsui MSF-818PC-NC CNC surface grinder.

#### Grinding wheel

For grinding samples, we use diamond abrasive surface grinding wheels from Norton. We use 6" diameter, 1/2" thick, 1-1/4" hole wheels. At the moment, we use a [320 grit wheel](https://www.mscdirect.com/product/details/90923806) for plunge grinding, which may even be too fine for this application and could be switched to a 220 or coarser grit in the future. To limit the appearance of scratch marks in 3D automated grinding and imaging work, we use a 400 grit wheel. The wheel was never listed on the MSC website, so contact Norton or MSC directly for a replacement. The part description is: 6X1/2X1-1/4 1A1 GRIND WHL ASD400-R75-B99-1/4QIA 

For balancing and truing the wheel, see the [Wheel balancing and truing](wheel_balancing_truing.md) section.

If there are ever any issues with surface quality when grinding, Norton tends to be very helpful in diagnosing the issue and sometimes recommending a different wheel if you contact them directly. Our most recent area rep was Ryan Chung. Ken from Millennium Machinery also recommended that we could reach out to Chuck Stormes at [South Bay Supply](http://www.southbayllc.com/aboutus/) for further adviece and even custom wheels.

#### Coolant

We try to keep coolant in the tank at > 6" depth at all times. When coolant is low, mix [Monroe AstroGRIND A](https://www.mscdirect.com/product/details/00267781) to 2.5% concentration with deionized water and pour into the tank through the filter paper. If you're doing a lot of grinding, the coolant should be completely replaced ~1 time per year. There is no great way to clean out the tank when replacing coolant, so just try to get as much out as you can with the crank pump, and scrape the rest out with something like a piece of cardboard. If you detach the pump wires from the tank, you can take it outside and try to open its valves to flush sediment out into the storm drain. Once the tank is empty and clean, refill with 2.5% coolant.

Every 6 months or so, it's a good idea to check the chemistry of the coolant, just in case anything wild is happening. We use [pH Test Strips](https://www.mcmaster.com/11235T62/), [Hardness Test Strips](https://www.mcmaster.com/11235T41/), and [Alkalinity Test Strips](https://www.mcmaster.com/11235T51/), and aim for readings around:
- pH: 10
- Hardness: 120 ppm
- Alkalinity: 240 ppm (Reading usually looks to be greater than 240, but that's the max listed on the container)

#### Autolubricator

Don't need to know much about the autolubricator (large wheeled module attached to the grinder through a few hoses). For maintenance, check the air filter on the front for dust every 6 months or so. If dusty, rinse clean in the sink. Check its oil levels, which should only have to be topped up to the yellow line 1x per year or so with [Red Mobil #6 Chiller Oil](https://www.grainger.com/product/4ZF38?gucid=N:N:PS:Paid:GGL:CSM-2295:4P7A1P:20501231&gad_source=1&gclid=Cj0KCQjwgJyyBhCGARIsAK8LVLPaWAsWm7SLFO9yRmcPppd6mvyLQ0vntz83gBcTBF1fW71n4ka5-i8aAgleEALw_wcB&gclsrc=aw.ds).

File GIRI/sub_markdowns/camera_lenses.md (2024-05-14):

## Camera

#### RCAM: 

The basis of our camera setup is a Digital Transitions RCAM, which is a solution for high-fidelity reprographic photography. This setup is common for libraries documenting/digitizing rare and important print works. The RCAM is basically a precision-machined metal tube that allows us to attach a medium-format digital camera back to one side, and a lenses (via lens boards and extension tubes) to the other side. 

#### Phase One IQ4 digital back: 
We upgraded to the Phase One IQ4 150 megapixel achromatic back in 2021. Prior to this sensor, we were using a Phase One IQ180 80 megapixel RGB back. This sensor gives the opportunity for high-resolution (~3.4um pixels) imaging of any lightwave in the back’s sensitivity range of ~400-1000nm. Note that the back itself has a digital shutter, so it should be complemented with lenses that have no shutter or have the shutter programmed to be constantly open. 

#### 120mm apochromatic Schneider-Kruznach Macro lens:
To achieve 1:1 macro photography, we use a 120mm Schneider-Kruznach APO-DIGITAR 5.6/120 M lens. This lens is apochromatic, meaning it is corrected for chromatic aberration in three wavelengths, and its wavelength vs. focal shift curve looks like a 3rd order polynomial ([figure](../photos/lens_info/chromatic_aberration.png)). We do have ways of assessing and correcting-for this chromatic abberation when doing multispectral imaging, see the supplemenary material of Manzuk, et al. 2022 for details ([link](https://gsapubs.figshare.com/articles/journal_contribution/Supplemental_Material_A_High-Resolution_Multispectral_Macro-Imager_for_Geology_and_Paleontology/19773532)).

Important note: the APO-DIGITAR 5.6/120 M lens no longer is in production, and we have not found a suitable replacement. THIS LENS MUST BE VERY WELL TAKEN CARE OF. The particular quality of the lens is in its focus flatness, that is, how it does not notably lose focus moving from the center to the edges of the image. We had tested a newer version of the lens, the aspheric, and found that it did not have the same focus flatness. A comparison of the two can be found in this [figure](../photos/lens_info/schneider_lens_comparisons.png).

We need extension tubes on this lens board to achieve 1:1 imaging. Specfically, between the lens board and the RCAm, we have a 30mm + a 40mm extention to give 70mm of extension. When installed, the setup should look like this [image](../photos/lens_info/lens_120mm_installed.jpeg). 

#### 72mm Schneider-Kruznach lens:

For larger field of view applications have a 72mm Schneider-Kruznach APO-DIGITAR 5.6/72 L lens. This lens is a lot less fancy, but achieves sharp images over an approximately 19 x 14cm field of view. 

This setup does not need to be installed with any extension tubes.

#### Wire grid polarizer:
Off-the-shelf, circular polarizers for photography only are effective in visible light. For broadband polarizing capability, we use a wire grid polarizer. We worked with a company Moxtek to create a custom solution that mounds to the 40.5mm filter thread of our lenses.

#### UV cut-off filter:
To avoid UV light contamination in our images, both due to any possible ambient sources, as well as when taking UV fluorescence images, we use a UV cut-off filter from Edmund Optics. The filter we use cuts-on at 390nm, and is monted on a 40.5mm filter thread ([link](https://www.edmundoptics.com/f/mounted-uv-filters/11546/)).

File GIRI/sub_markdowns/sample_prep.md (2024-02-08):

## Preparing a sample for serial grinding and imaging

1) This recipe assumes that your sample is well lithified or epoxy-injected such that it will withstand the grinding and imaging process without falling apart. For vacuum injection of epoxy into samples, contact [Wagner petrographic](http://wagnerpetrographic.com). We have had some luck mounting loose grains like ooids ourselves by 3D printing one of the boxes below and successively layering the grains in this [table top epoxy resin](https://masepoxies.com/product/table-top-epoxy?gclid=Cj0KCQjwsp6pBhCfARIsAD3GZuZvY6Mlc-rvrGY6VEFGhych-UP304RyY_hcOdk5y4VX3xdpKuVCHMcaAr-fEALw_wcB)

  * [simple box](../cads_drawings/sample_embedding_boxes/epoxy_box.stl)<!-- {"embed":"true"} -->

  * [sectioned box](../cads_drawings/sample_embedding_boxes/ooids_box.stl)<!-- {"embed":"true"} -->

2) Saw your sample down to size such the horizontal dimensions are roughly the size of the imaging field of view you plan to use. No need to grind superfluous rock, but a little extra is okay. Generally, rectangular prism shapes are easiest to work with, and certainly try to ensure that the top and bottom surface are close to parallel. If working with an oriented sample, I find it easiest to work with having the top surface be the oriented surface such that you know the orientation of your imaging plane and can do all later rotations with respect to that (just be sure the orientation mark is captured in one of the first images for record keeping).

3) With your sawed sample, you’re ready to mount it to a steel plate. We use 1/4” low-carbon steel sheets from McMaster-Carr. The most common dimensions we use are [3x3”](https://www.mcmaster.com/1388K102/), [3x6”](https://www.mcmaster.com/1388K106/), and [4x4”](https://www.mcmaster.com/1388K104/). Just pick a size such that your whole sample fits without much or any overhang. Sand the top surface of the steel plate and the bottom surface of your sample with coarse (~60 grit) sand paper so there is a rough surface for the epoxy to grab onto.

4) Rinse the sanded surfaces with water to remove grit, and blow dry with an air hose.

5) Put on gloves and extrude enough [2 ton epoxy](https://www.mcmaster.com/66215A24/) into a mixing cup to coat the whole bottom surface of your sample. 3-4 pulls of the trigger tends to be plenty for most samples. 

6) Mix the epoxy with a popsicle stick for at least 2 minutes.

7) Use the popsicle stick to apply a coat to the bottom surface of the sample and place the sample on the steel plate. I tend to then apply any extra epoxy to the corner where the sample meets the plate as extra reinforcement. 

8) Allow the epoxy to cure for at least 24 hours. (You can remove the gloves at this point).

9) Before placing the sample on the machine, de-bur and smooth the bottom surface of the steel plate by applying [sharpening stone oil](https://www.amazon.com/Norton-Abrasives-07660787940-Sharpening-Stone/dp/B000I1AVDW/ref=asc_df_B000I1AVDW/?tag=hyprod-20&linkCode=df0&hvadid=198090983914&hvpos=&hvnetw=g&hvrand=2480446956776683294&hvpone=&hvptwo=&hvqmt=&hvdev=c&hvdvcmdl=&hvlocint=&hvlocphy=9003941&hvtargid=pla-384768754761&psc=1) to the surface and polishing it with the coarse (red) sharpening stone in a figure 8 pattern. It may be tough to move the stone at first, but it should ease up as the plate gets de-burred. Once the stone glides fairly easily over the plate surface, you can switch to the fine (gray) sharpening stone to finish up with 10 or so more passes.

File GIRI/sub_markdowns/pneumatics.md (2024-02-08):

## Pneumatic peripherals
#### Camera shutter
#### Sample roller

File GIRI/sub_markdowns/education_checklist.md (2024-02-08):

## Checklist of things to learn/know for operation
- [ ] Wheel balancing
- [ ] Wheel truing and dressing
- [ ] Dusting the chuck (or other metals)
- [ ] G code
  - [ ] Writing simple G code for automated ginding/flattening protocols
  - [ ] Navigating main G code of 3D sample processing with imaging
- [ ] The basics of surface grinding
  - [ ] Manual grinding
  - [ ] Tips and tricks for achieving a good finish
- [ ] Daily Maintinence
  - [ ] Coolant
  - [ ] Machine oil
  - [ ] Compressed air systems
- [ ] Longer term Maintinence
  - [ ] Autolubricator
- [ ] Epoxy mounting samples to metal plates
- [ ] Setting up a new sample run
- [ ] RCAM operation and changing lenses
- [ ] Continuing to run a sample
- [ ] The grinder control computer
  - [ ] data storage and backup
  - [ ] GIRI’s operation code base
    - [ ] Matlab
    - [ ] C++ SDk
    - [ ] Capture One Processing Engine  
  - [ ] Capture One
- [ ] PLC
  - [ ] Basic wiring and rationale on setup
  - [ ] Writing ladder logic in Connected Components Workbench
  - [ ] Ring and brick lights

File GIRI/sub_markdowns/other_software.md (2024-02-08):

## Other software

#### Capture One
- To manually control the camera and view raw images, we use Capture One. Versions often change, best to be using the latest. See offline documentation for credentials.

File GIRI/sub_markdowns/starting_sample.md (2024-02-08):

## Mounting a new sample for serial grinding and imaging

1) Turn on machine switch on front of machine. If air is coming out of the valve on the right of the machine (loud hissing noise), place a finger over the valve. The hissing should stop. 

2) Turn on the camera. 

3) On the onboard computer, select “jog” and the “10x” handle command. Move table to the left using the z-axis wheel, such that most of the magnetic chuck is to the left of the wheel. Then select “auto” within the jog menu for the machine to recenter itself. We move the table to the left prior to auto-centering the positions because if the table is too far to the right, it may jog itself past its limit and throw an error.

4) On the onboard computer, go back to the main menu and select “G code.” Using the 10x and 1x toggles on the computer, bring the table z-axis (left and right) near -1.00000 in machine coordinates. After, make sure to deselect the 10x or 1x toggle so that the table does not move. We want the table around this position because that is where the grinder moves to image in the grinding and imaging protocols. No need to be very exact for now, this step can just help give you a rough guide for initially placing the sample.

5) If you have not yet, now is a good time to use the fine honing stone and [3-IN-ONE oil](https://www.grainger.com/product/3-IN-ONE-Machine-Oil-Multipurpose-Oil-4UJ34) to polish the chuck. Use a figure 8 pattern to move back and forth on the chuck. 5 passes each way should be enough.

6) Rub some [3-IN-ONE](https://www.grainger.com/product/3-IN-ONE-Machine-Oil-Multipurpose-Oil-4UJ34) oil on the machine chuck and on the bottom of the sample plate. Place the sample on the chuck in a position you think would be in the camera field of view, directly below the lens. Do not engage the magnet yet.

7) We now want to set the starting point in the y-axis (up and down) such that the wheel starts just above the highest point of the sample to avoid having to do hundreds of grind sequences before making contact with the sample. Then, using the 10x and 1x toggles on the computer, move the table down (y-axis) so the sample is well below the wheel. Move the table left-right, forward-back (z and x-axis) until the highest point of the sample is under the lowest point of the wheel. Then move the table up (y-axis) until there is less than a millimeter of space between the wheel and the highest point of the sample. Do so slowly and carefully, as a collision between the wheel and the sample may damage or even shatter the wheel. Once the wheel is close to the sample, bring the table z-axis back to exactly -1.00000 machine coordinates. Ensure the movement toggles are off. 

8) We use the imaging position (which is where the table currently is positioned) as the relative 0 in the G code for grinding and imaging. Set this position as the 0 now by selecting “pos” and within that menu select “all” and “0 set.” Close this menu.

9) Now we’ll make sure the sample is well-positioned in the field of view. This step requires the live feed, so if the mechanical shutter is in front of the lens, open it from the onboard computer main G code menu by selecting “FUNC1.” In that menu, under the “others” group, it is the “MAG” button.

10) On the control iMac, in Capture One (whichever version is current, shouldn’t matter), select the live view (the button that looks like a video camera). The feed should show the view from the camera. Gently slide the sample plate around on the chuck until the desired portion of the sample is within the camera’s field of view. Sometimes I turn the iMac around so I can see the feed while positioning the sample.

11) Once the sample is well-positioned, engage the magnetic chuck by flipping the lever to the right and close the shutter using the same command that you used to open it.

12) **Update this section once housing is finalized for new setup with ring light**

13) Time to set the starting position and the width of the sample in the x-axis (forward to backward when looking at the machine). Move the table in the x-axis until the wheel is just in front of the front edge of the sample (when standing at the front of the machine where x-axis movements are forward-backward). Sometimes it is easiest to verify this position standing near the onboard computer, looking down the z-axis. It is best to leave a few millimeters of space just to be sure the entire sample will be ground. This position is where the wheel will start a grind before moving across the sample, so extra space in this direction just adds to the time-per-grind. Not a huge deal to have extra, but don’t go crazy. Set this position to x = 0 in relative coordinates (“pos” -> “relative” -> by x select “reset” and type in 0). 

14) Enter the sample width into the G code. You can figure out sample width by moving the table on the x-axis until the wheel is behind the back edge of the sample when standing at the front of the machine. The absolute value of x in relative coordinate space is the width of your sample. You can add a few tenths of an inch just to be safe. In this case, don’t add more than a couple of tenths because superfluous movement in this direction will add time between the sample finishing grinding and moving to the roller and imaging, increasing the risk of drying before imaging. To put the sample width into the G code, find the line that reads “G91G01X_._F150. /* Move across sample…” Your sample width in inches with one decimal place will go in the blanks after X (using G code from a previous sample, the blanks will be populated with the width of the previous sample). Move the table along the x axis back to 0 in relative coordinates. Be sure to then turn off the x10 or x1 movement toggle.

15) Save the G code file. Select save near the top of the screen. Rename the file in the format “samplename.startdate” and save it. It can help to plug a keyboard into one of the usb slots on the computer to make typing easier.

16) The final step is Left and Right teaching so the machine knows which coordinates to move between on the z-axis when passing over the sample to grind it.. To do this, move the table along the z axis until the entire sample is to the left of the lowest spot on the wheel. An extra inch or so is a good idea. When you are at a good left-most position, hit “L teach” on the screen. Then move the entire sample to the right of the lowest part of the wheel, again leaving an extra inch or so, and hit “R teach.” When this is done, move the sample back to z=-1.000 in machine coordinates (should be 0 in relative coordinates).

17) You are now ready to start grinding. You can follow the next section: ‘[Daily operations to grind and image a sample](daily_operations.md)’ to get going.

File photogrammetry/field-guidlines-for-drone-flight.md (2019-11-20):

# Guidelines and Helpful Info for Flying the Drone

### Before leaving princeton

### GCPs
- bring or purchase blue tarps from a hardware stores
- if you don't have enough space for tarps, you can use natural landmarks, but make sure they are really big (meter scale) landmarks
- try to put GCPs in the corners of the flight areas
- if you are placing the tarps, bring the Trimble with you and take the trimble points as you set out the tarps
- Cars make excellent GCPs--But you have to make sure they aren't moving during the flight (Don't use Frederik's car as a GCP)

### Preflight
- Put in a new SD card
- Turn on the radio transmitter
- Take off the lens cap

### If the drone crashes
- look at the last known GPS location in eMotion

### Processing data in the field

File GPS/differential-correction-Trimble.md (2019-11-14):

# Differential Correction of Trimble Data

### Important Contact Info
Manager the GPS Pathfinder Office Licenses:  
Bill Guthe  
PHONE: 609-258-4609  
EMAIL ADDRESS: wguthe@princeton.edu  
OFFICE LOCATION: 332 Lewis Library

### What you need:
- Floating License of GPS Pathfinder Office
- VPN set up in case of issues with Pathfinder
- Trimble Rover
- SD card in Trimble
- Micro-USB to USB/USB-C (Normal Micro-USB cables do not fit into the Trimble, you have to use a pocket knife to cut part of the rubber around the Micro-USB end so it will fit into the Trimble)
- batteries
- charging cable

### Before Going to the Field
#### 1. VPN
Make sure you have a VPN on the computer you will use in case you run into any issues with the GPS Pathfinder license. Below is how to do it for Windows 10. But you can get instructions by just Google-ing 'Princeton University VPN'.
1. go to https://remote.princeton.edu
2. Select "Princeton University" for the "Log in to:" field and click **Next**
3. Enter your PUID and password
4. Install Connect Tunnel
5. Click **Save File**, then double click "setup65.exe" and install the software
6. Once installed, restart the computer. Click **Yes** to complete the installation.
7. To login to VPN, type "SonicWall" in the search box in the bottom left of your screen and double-click **SonicWall VPN Connection APP**
8. If this is the first connection, you may need to type in "remote.princeton.edu" for the servername.  Then, enter your Princeton netID and password, then click **Connect**.
9.  You will receive a Push or Call to your primary Duo device. While SonicWall is waiting for approval from Duo, you will see a “Connecting...” windows displayed.
10.  Your System Tray will momentarily notify you of a successful connection.
11.  To disconnect from Secure Remote Access, right-click the Sonicwall VPN Connection or Princeton Secure Remote Access shortcut on the Desktop or System Tray icon and select Disconnect.

#### 2. Check-Out Floating License
- Open the application, <u>GPS Pathfinder Office License Administrator</u>.
- Select **Floating**, the server address should be "cseslicense02.princeton.edu".
- click **Borrow License...**
- Select **4 Weeks**, and **Borrow Now**, a window should pop up saying 'The License was borrowed successfully'.

#### 3. Testing
###### VERY IMPORTANT:
Take the computer off campus (not on campus WiFi) and try to go through the entire differential correction process before leaving Princeton.

## Differential Correction
#### 1. Import Data From Trimble
Easiest to do by plugging the Trimble into the computer, but can also be done with the SD card. Following instructions are for when the Trimble is plugged into the computer.
- Plug in Trimble to computer
- Select **Utilities** --> **Data Transfer**
- Make sure the Device selected is "GIS Datalogger on Windows Mobile", then press the button just to the right with the green check mark.
- Click **Add**
- Then select your data and import

#### Differential Correction
- From the **Utilities** tab, select **Differential Correction**
- Choose the file you wish to correct, and press **Next**
- Use **Automatic Carrier and Code Processing (Recommended)** and **Use a single base provider**, click **Next**, and **Next** again.
- Click **Select** in the Base Provider Search
- Press **Update List**,  then choose a base station close to where your data is, then select **OK**, then select **Next**. **NOTE: I have had the best luck with stations that have both L2 and G files**
- Use the defaults for the output folder and filename. Select **Start**, when it finishes, select **Confirm**.
- When it finishes, copy the 'Differential Correction Summary' and save it in a .txt with named 'fieldsite-year-summary.txt' (i.e. amato-2019-summary.txt).
- Press **Close**

#### Export
- On field computer in Lenovo ThinkPad Carbon we are using in 2019, use 'Export to .CSV' as the export setup and press OK
- If you are using a different computer,  press **New...**
- In the New Setup Window, create your name, make sure 'Configurable ASCII' is selected in the 'New Setup', Click **OK**
- Click **Configurable ASCII** tab
- click **New** under template list and give the template a name, **OK**
- make sure **points**, **lines**, and  **area** are selected. 'Field Format' is 'Delimited', use preset delimiters.
- type in file extension, 'csv'
- check on 'Use Template as Heading'
- In 'Macro Palette', select **Feature ID**, **Feature Name**, **Lattitude**, **Longitude**, **Northing**, **Easting**, **HAE**, **MSL**,  **Attributes**, **GPS Time**.
- Click **OK**
- click 'Attirubtes' Tab
- Under 'Point Feature', turn on: **Height**, **Vertical Precision**, **Horizontal Precision**, **Standard Deviation**, **Position**, and **Point 1D**.
- Under 'Line Feature', turn on: **Length (2D)**, **Length (3D)**, **Average Vert. Position**, **Average Horiz. Precision**, **Worst Vert. Precision**, **Worst Horiz. Precision**.
- Press **OK** and then **OK** in the export window.
- This produces a '.csv' called 'Point_generic.csv' in the Export Folder of your working directory. Change the name of the '.csv' to the field locality and year. (i.e. 'amato-2019.csv').

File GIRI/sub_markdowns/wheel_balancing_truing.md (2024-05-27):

## Wheel balancing and truing (and dressing)

#### General notes:
- This document specifically deals with preparing resin-bonded diamond grit wheels. The process for preparing the silicon carbide wheel for chuck dressing is detailed [here](chuck_dressing.md).

- The general purpose of balancing and truing a wheel is to ensure the wheel is round and rotating evenly on the spindle. Having a round, balanced wheel helps prolong the life of the spindle, and helps achieve a quality finish on the sample with minimal scratches.

- This process should be done:
    - When the wheel is brand new
    - When a wheel has been removed from its collar in between stints of grinding
    - When a wheel has been grinding for a few months consistently and the quality of the finish is degrading

- Schools of thought vary as to if you should re-balance the wheel after truing. Lately, I've been having fine results just balancing first and then truing (some say you should not think about removing and re-balancing the wheel after truing because that's the most in-round it will be). In general, I would maybe just repeat a balancing + truing cycle if the finish is not up to par.

- After truing, the WHEEL MUST BE DRESSED (detailed below) to open up the grit to cut.

- When handling wheels and balancing equipment, be very careful not to drop anything. Wheels are fragile and could break on dropping. The collars and axel used in balancing are also precision machined and should be handled with care as drops could damage their function.

---

#### Balancing the wheel:
Note: we have one of the less sophisticated balancing setups, so resources aren't too available online. This [video](https://www.youtube.com/watch?v=yYBXmqEU2r4&t=431s) shows the process with a similar setup. In the video, they drill the wheel to remove weight and improve balance, which is different from our weight sliding setup.

1) Install the wheel on its collar, using the specialized spanner wrench and hook wrench to achieve a secure fit.

2) Get out the balancing stand and check that it is level, probably best to level with a bubble or electronic level separate from the one on the stand. If you have difficulty achieving a level stand on the grinder lab work bench, you can try the Starrett granite slab in the machine shop.

3) Attach the axel included with the balancing stand to the wheel collar. Note the axel can only be attached in one orientation, so if it's spinning weirdly on the stand flip it around (update this section with the correct orientation during the next balancing session).

4) Start the process of checking balance placing the axel/wheel setup on one end of the stand and gently pushing it in the other direction to observe how it spins. The goal with the push is to give it enough momentum where it would barely make it to the other side of the stand. Any lurches or unevenness in speed as the wheel spins is an indication of imbalance.

5) To start honing on a balanced wheel, give it a roll where it does not make it to the other side of the stand. The wheel will stop, and you can treat the side that was down as the hypothesized heavy side. In its stopped position, mark the top of the wheel with a sharpie (antipodal to the heavy side, the top is just easier to see/mark). To test if this indeed is a heavy spot that needs to be corrected, you can either give the wheel another roll and wait for it to stop, or just bring the heavy side to the top (rotate the wheel 180 degrees) and release it to see if it immediately falls to the bottom and starts rotating. In either case, repeated settling of the same spot at the bottom (sharpie mark at the top) is a good indication that this is the heavy side.

6) To correct the imbalance, use an allen key to loosen the set screw in the weights that are nearest the heavy slide, slide them towards the lighter side, and tighten the set screw. You may have the best luck moving just one weight at a time and rechecking balance or moving multiple. Balancing is an imperfect science, just trust your intuition of moving weight away from the heavy side and making small adjustments when the wheel seems pretty close to balanced. 

7) Once the wheel is able to roll smoothly and can make it to the other side of the balancing stand even when given very little starting momentum, it's probably pretty well-balanced. Lately, even brand-new wheels have been pretty well-balanced with mostly evenly-spaced weights and only minor adjustments needed from there. If the process is taking overly-long, double-check the stand is level, because any slope there could hinder judgement of how the wheel is rolling.

8) Once you are satisfied the wheel is balanced, remove it from the axel, give the axel a thin coat of petroleum jelly to prevent rust, and carefully pack everything away. 

#### Truing the wheel: 
For further guidance in truing, you can watch one of the best Youtube [video](https://www.youtube.com/watch?v=V53EdcG35TA&t=404s) of all time. The video is very informative about the goals and processes of truing and dressing. It specifically starts the instruction on truing at 6:00. The process that they start with of tapping the wheel initially while checking for run-out with a dial indicator to will not be detailed here, but you could consider adding it to the process, especially for newer wheels.

1) SAFETY GLASSES ON

2) Install the wheel on the spindle, hand tightening the (reverse-threaded) nut to start, and then using the hook wrench and tube wrench to secure the wheel. The wheel will self-tighten as it spins, but might as well get it good and tight to start.

3) Raise the wheel (y-axis) so you can comfortably fit the brake-controlled truing device underneath. I usually then start the wheel and let it spin for a minute or so, just to warm up and self-tighten before truing. Now also is a good time to run a red crayon over the wheel while it's rotating. The red crayon will serve as a visual indicator of the high spots on the wheel as you true.

4) With the grinding wheel no longer spinning, install the brake-controlled truing device on the chuck directly below the wheel. Most importantly, make sure the diamond the spin axis of the truing device and the grinding wheel are parallel. The grinding wheel should be at least a few centimeters above the truing wheel at this point. Secure the truing device by engaging the magnetic chuck.

5) Turn the spindle/grinding wheel on, at the same speed you would use for grinding. 

6) Slowly start lowering the grinding wheel towards the truing wheel, making adjustments in the z-axis as needed to position the lowest point of the grinding wheel directly above the highest point of the truing wheel. DO NOT COME WITHIN ~1mm MAKING CONTACT YET.

7) You're now ready to start the truing process. Now is a good time to make sure you have a feed rate setup that will work for you. You'll probably want the x-axis feed rate to be at the x10 setting at the top of the screen, and the y-axis feed rate to be at the x1 setting. If you think it will be annoying to have to flip these when switching which axis you're adjusting, open up the jog menu and set the desired feed rates for the axes individually there. (you could stop/raise the grinding wheel while you get comfortable with the feed rates)

8) With the grinding wheel on, and positioned directly above the truing wheel (both in terms of x and z-axis), probably feeding it a few ten thousandths at a time. You don't want it to make contact while the truing wheel is stationary, so a little before contact is starting to feel imminent, get the truing wheel spinning counterclockwise before each burst of lowering the grinding wheel. Also be ready to work the x feed as contact becomes imminent. Once the wheel starts to make contact, use the x feed to move the grinding wheel across the truing wheel first clear to one side, then back the full width to the other.

9) At this point, I find it helpful to keep track of positioning, so I know how much truing I have done. Hit the position menu and 0 set all relative positions.

10) Time to make successive truing passes. The video says you can lower 0.001-0.002" per pass, but I find that to be a bit aggressive, so I tend to stick to 0.0005" per pass. Before each pass, make sure the truing wheel is spinning, and pass the grinding wheel across the full width of the truing wheel, and back. At some point, try to switch which side of the wheel you are starting passes with to ensure even truing. You also can occasionally bring the wheel up slightly, bring it over in x to the middle of the truing wheel, and drop it slowly to contact the truing wheel to start a few passes in the middle, again to ensure even truing. (sometimes you can get a nice rhythm going where you never have to start the truing wheel spinning with your hand because you're following quickly enough with the next pass that it's still spinning from the previous pass)

11) Depending on how it's feeling/sounding, you might want to stop the spindle after the first ~10-15 passes to check the crayon on the wheel and see how even it's getting. Otherwise, continue truing with the different styles of passes until the crayon is mostly gone. Depending on the state of the wheel prior to truing, hopefully this doesn't take more than 30-40 passes total.

12) Once you're satisfied with the truing, stop the spindle, raise the grinding wheel, and remove the truing device. The wheel is now ready to be dressed.

#### Dressing the wheel:
Dressing the wheel also is touched on in the Youtube video linked for truing. 

1) SAFETY GLASSES ON

2) Turn the spindle on, and get dresser sticks soaking up some coolant.

3) Starting with the coarsest stick, manually push the end of the stick into the wheel. I tend to do this at a bit of an angle, working from one side to the other and alternating starting sides. You'll want to make sure you're getting the full width of the wheel, and not just the center or edges.

4) After a few passes with the coarse stick, switch to the medium stick, and then the fine stick. You'll probably want to do 5-10 passes with each stick. The video says a half stick per dressing, but we have thicker sticks, so it's a lot less. Technically, you should finish with a stick that is 1-2 grit sizes smaller than the wheel, but 400 is the finest dresser stick we could find, so we just finish with that, even for the 400 grit wheel. It works fine enough.

5) Ready to grind. Keep an eye on cutting performance and quality of finish as you start to process samples. If you're not getting the finish you want, you might want to repeat the balancing and truing process.

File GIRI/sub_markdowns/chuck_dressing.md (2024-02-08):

## Dressing the magnetic chuck

In general, refer to this [video](https://www.youtube.com/watch?v=ChH6ORg3Iq0&t=370s) for a good overview of chuck dressing. The video covers pretty much everything in this document.

Prior to dressing the chuck, you must prepare a silicon carbide wheel, so this document will be split into two sections: wheel preparation and chuck dressing.

#### Silicon carbide wheel preparation

The video linked at the top covers some wheel prep, but this [video](https://www.youtube.com/watch?v=MofRhM_W-Vk&t=652s) has a bit more detail specifically about carbide wheel dressing.

1) Safety glasses on!

2) Assemble silicone carbide wheel and balance according to instrctions in the [wheel balancing and truing](sub_markdowns/wheel_balancing_truing.md) section.

3) Mound the wheel on the spindle.

4) Place the single point diamond dresser on the chuck under the lowest point of the wheel. If anything, the dresser should be on the left(downstream) side of the wheel. The dresser has a lean to it, so make sure the lean is in the downstream direction for the wheel, which means it should be leaning leftward.

5) Engage the magnetic chuck and turn on the spindle.

6) Slowly lower the wheel to be just above the highest point of the diamond. 

7) At this point you're read to dress the wheel. Prepare the axis jog increments such that you can move fairly quickly along the x-axis (like a normal feed rate), and such that clicks on the y-axis movement wheel are 0.001".

8) Continue to lower the wheel slowly over the dresser, moving at 0.001" increments in the y-axis. 

9) Once you hear the wheel start to make contact with the diamond, move along the x-axis at a normal feed rate such the entire wheel with passes over the dresser.

10) Continue to make passes of the wheel over the dresser, dropping the wheel by 0.001" increments in the y-axis each time. At first, while the wheel may be out of round, you will possibly hear chatter. Listen for the chatter to go away with each pass, as you can stop dressing the wheel when the sound with each pass is a smooth, unbroken hum. Getting a trued wheel should only take a few passes. Once the wheel sounds trued, perform 2 more passes, but only drop the wheel by 0.0005" for each.

11) Turn off the spindle.

12) The wheel is close to ready. For an ideal finish on the chuck, you should now remove the wheel from the spindle and re-balance it. Once the wheel is re-balanced, put it back on the spindle and lower it over the dresser again. Now, you should only need to make 1-2 passes, with the wheel dropping by 0.0005" each time. This slight repeat of the procedure helps to ensure the wheel is perfectly round and balanced.

13) Disengage the chuck to remove the dresser. Before putting the dresser away, be sure to loosen the diamond from the holder and rotate it 90 degrees. This will help to ensure the diamond wears evenly.

#### Dressing the chuck

1) Safety glasses still on!

2) Turn on the magnetic chuck. You always want to dress with the chuck on because this will harden the chuck, so it won't heat and warp during dressing.

3) Dressing the chuck will be easiest if you know where the highest point on the chuck is. You can find this by using a dial indicator. Attach the indicator magnetically to the spindle housing, and set the indicator to touch the chuck. Use the grinder feeds to move the chuck under the indicator, and note the highest point.

4) Bring the wheel over the highest point and lower close to the chuck, without making contact.

5) At this point, turn on the spindle and coolant. Coolant should be on at all time to dissipate any heat during dressing. Heat is bad because it can cause the chuck to warp.

6) Lower the wheel VERY SLOWLY, with increments in the y axis of 0.00001". Chuck dressing is not an aggressive grinding process. Continue to lower slowly, listening for the sound of the wheel on the chuck. At such a slow rate, it may take a while, but be patient. NOTE: if you were not able to find a definitive high point on the chuck, left and right teach the table such that when you start the table, it runs the entire length of the chuck. Do this lowering process with the table moving, only lowering the wheel by 0.00001" per pass.

7) Once you hear the wheel make contact with the chuck, I would raise the wheel up by 0.0002", just in case finding the high point was not perfect. 

8) 0 set all relative positions so you know where you are, especially in the y-axis.

9) With the coolant and spindle on, run the G code program `mag.chuck.dress`. This program starts on one corner of the chuck and moves along the entire length of the chuck in the z-axis before stepping over in the x-axis and returning in the z-axis. The program itself does not lower the wheel.

10) Once the program has completed its first pass over the chuck, you can lower the wheel. Never lower the wheel by more than "half a tenth" (0.00005") at a time. Again, this process is not aggressive. After lowering the wheel, run the program again.

11) As you make passes and lower the wheel, you should start seeing the wheel in contact with more and more surface area of the chuck. There may be some sparks as it makes contact, but it should not sound or look too aggressive.

12) Continue to make passes and lower the wheel until you have dressed the entire chuck. Then, without lowering the wheel, run the program at least 3 more times to ensure the entire chuck has been dressed and any potential warping has been removed.

13) Once you are satisfied with the dressing, turn off the spindle and coolant. Disengage the chuck and remove the wheel. Chuck dressing is complete.

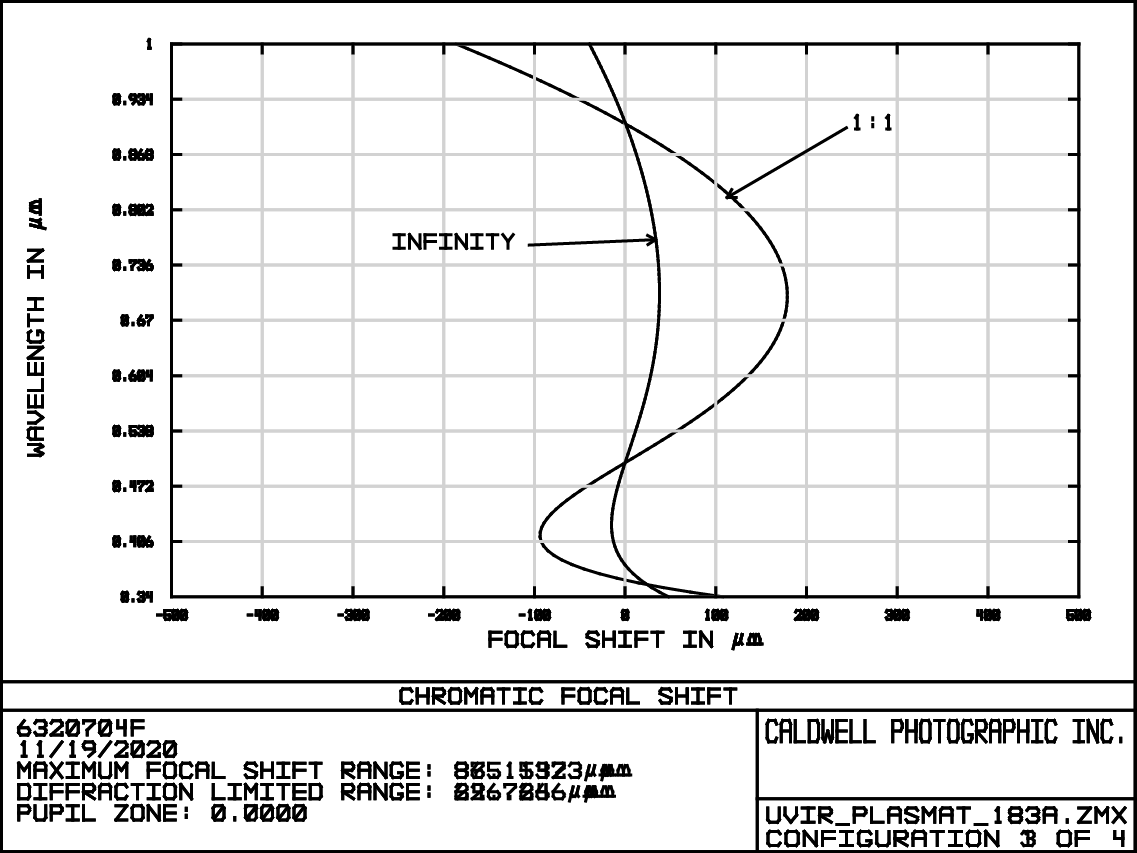
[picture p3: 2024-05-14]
GIRI/photos/lens_info/chromatic_aberration.png

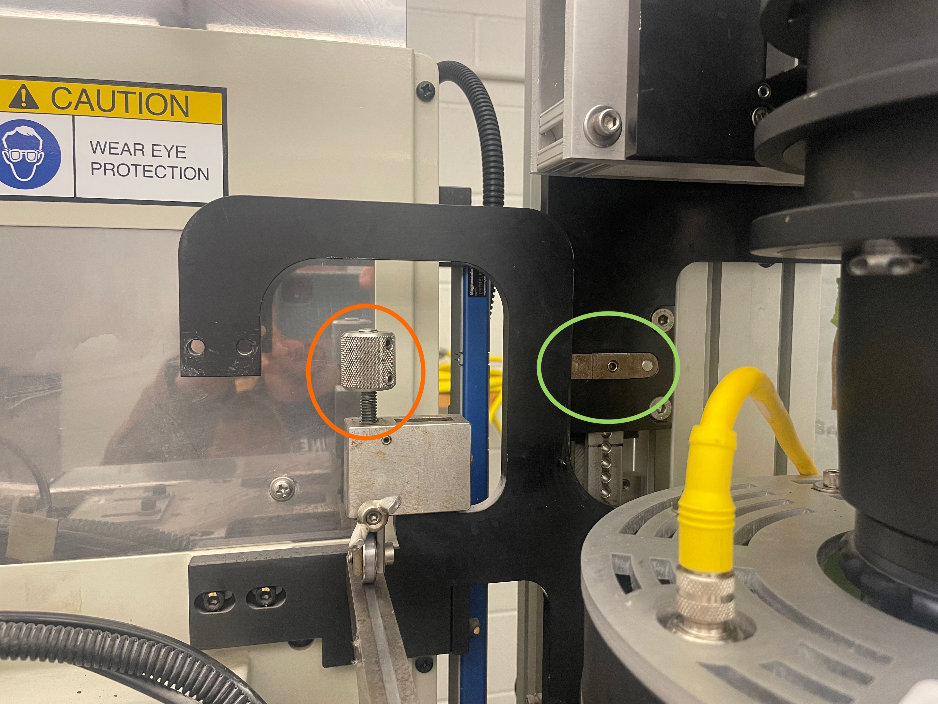
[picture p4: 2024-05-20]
GIRI/photos/camera_focus.jpg

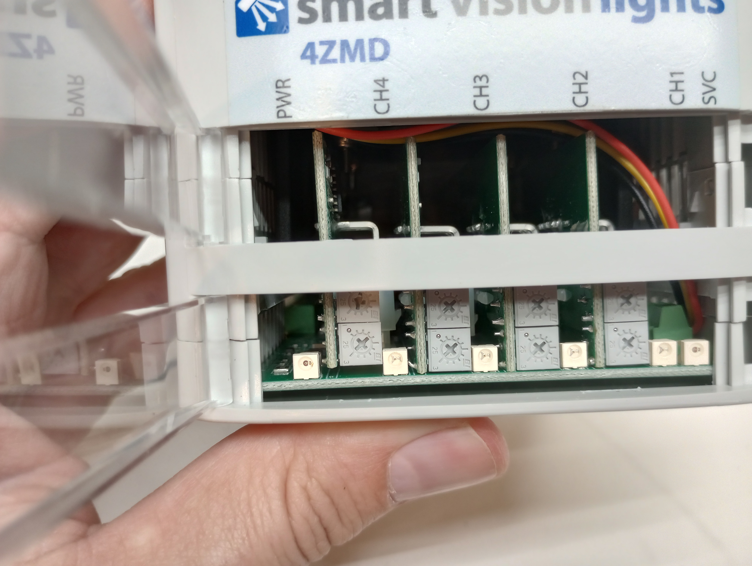
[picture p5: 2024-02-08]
GIRI/photos/4zmd_fix/4zmd1.jpg

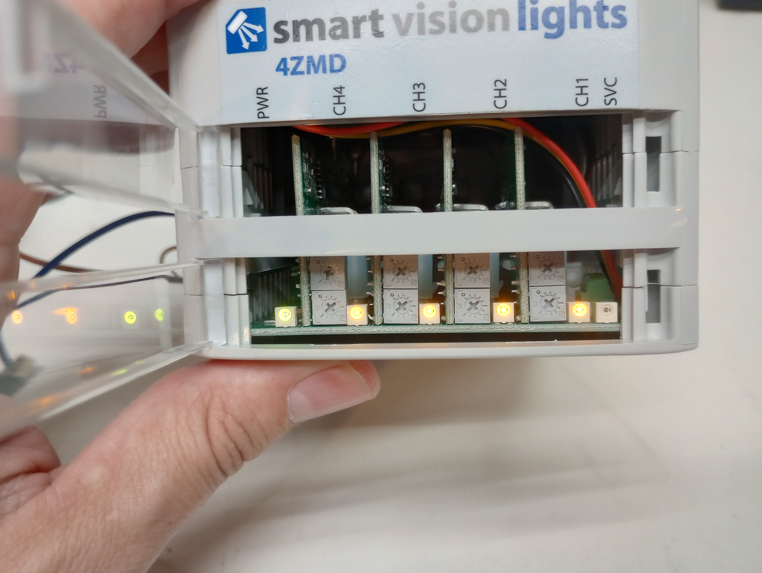
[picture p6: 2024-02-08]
GIRI/photos/4zmd_fix/4zmd3.jpg

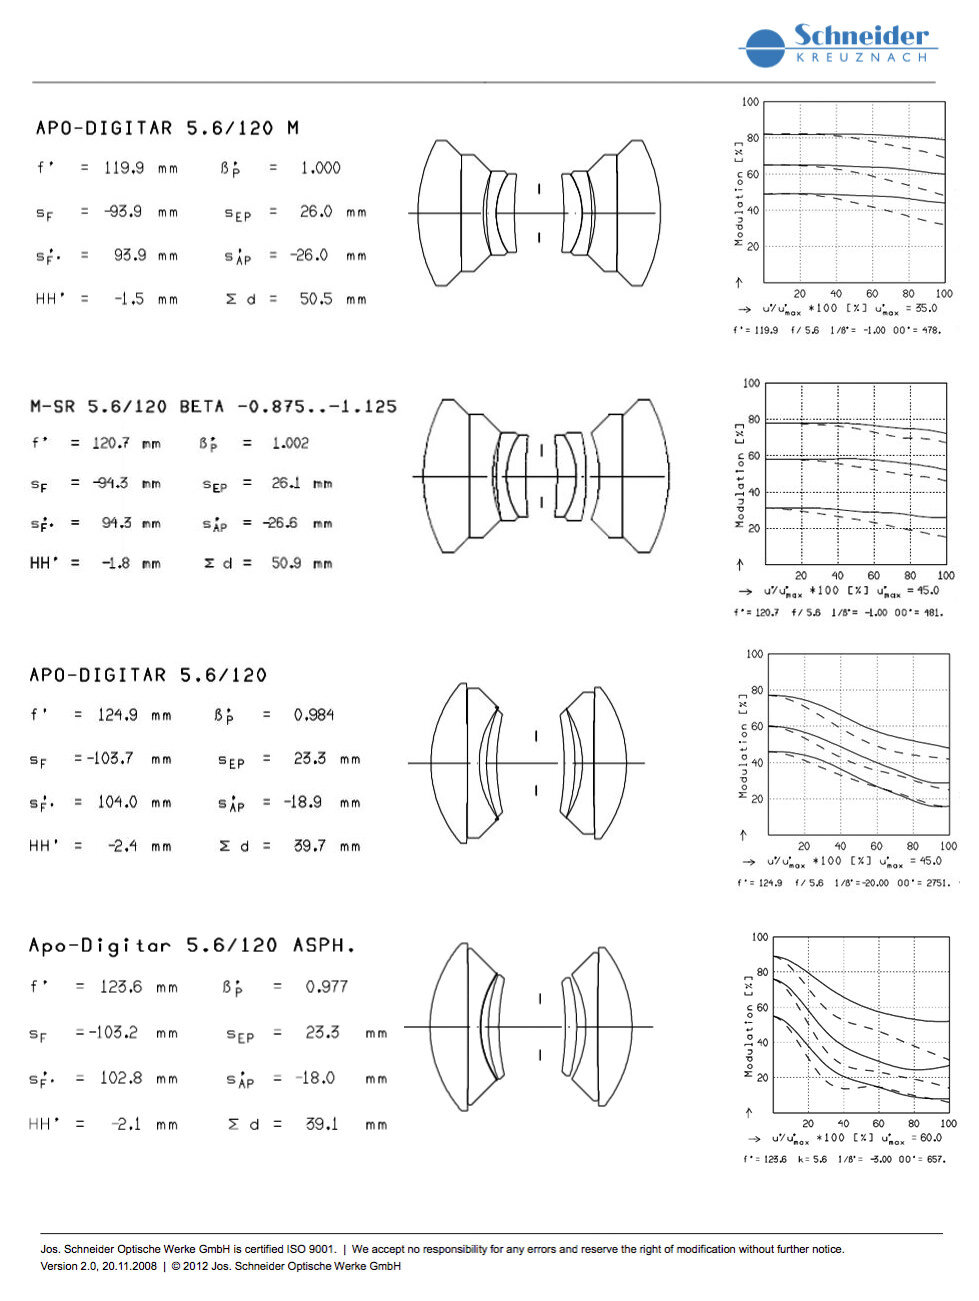
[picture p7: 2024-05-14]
GIRI/photos/lens_info/schneider_lens_comparisons.png

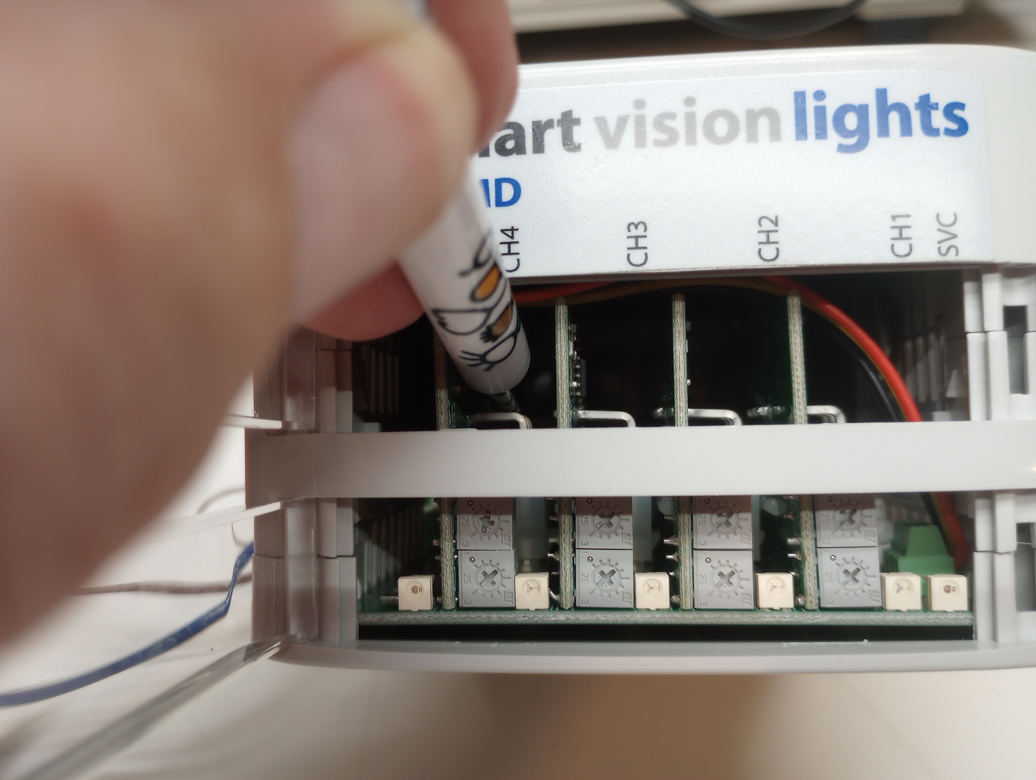
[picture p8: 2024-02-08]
GIRI/photos/4zmd_fix/4zmd2.jpg

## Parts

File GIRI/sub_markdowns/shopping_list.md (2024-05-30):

## Summary of maintenance products

Although these products are listed throughout this documentation, this specific MD is meant to succinctly summarize all products needed to keep GIRI running, where to buy them, and how often to use them (if applicable).

#### CNC maintenance
- [Mobil Vactra #2 Way Oil](https://www.amazon.com/Mobil-100772-Vactra-No-2-Way/dp/B07B7XZKVF/ref=sxts_b2b_sx_reorder_acb_business?content-id=amzn1.sym.f63a3b0b-3a29-4a8e-8430-073528fe007f%3Aamzn1.sym.f63a3b0b-3a29-4a8e-8430-073528fe007f&crid=IC2CPFO8QUUC&cv_ct_cx=mobil+vactra+oil+no.+2&dib=eyJ2IjoiMSJ9.mwqFczy3TS-udy-PQdVb5Q.FFxRISToPoJwxay2ygkvVPyxLYVUrZprHFEgPiLLcW0&dib_tag=se&keywords=mobil+vactra+oil+no.+2&pd_rd_i=B07B7XZKVF&pd_rd_r=38587f78-a786-44df-818e-cdda64d64c3f&pd_rd_w=YQ7zF&pd_rd_wg=iOvJH&pf_rd_p=f63a3b0b-3a29-4a8e-8430-073528fe007f&pf_rd_r=8DDYMRVNSP9F8M05S5YC&qid=1715974664&sbo=RZvfv%2F%2FHxDF%2BO5021pAnSA%3D%3D&sprefix=%2Caps%2C66&sr=1-1-9f062ed5-8905-4cb9-ad7c-6ce62808241a) - Probably should top up ~1x per week when machine is running actively (be sure to check the tray in the back of the machine for waste oil). (This goes in reservoir on the front of the grinder.)
- [Monroe AstroGRIND A](https://www.mscdirect.com/product/details/00267781) - Probably should top up (diluted to 2.5%) every couple of days when running actively, depending on the sample. Protocol: do not start run if <6" of coolant. We use DI water.
- [Filter Paper](https://www.millenniummachinery.com/contact-us/) - Product number PFMSTP50, need to request quote from Millennium Machinery (linked). I would say a full roll lasts 9 months or more, depending on how much you're grinding.
- [Red Mobil #6 Chiller Oil](https://www.grainger.com/product/4ZF38?gucid=N:N:PS:Paid:GGL:CSM-2295:4P7A1P:20501231&gad_source=1&gclid=Cj0KCQjwgJyyBhCGARIsAK8LVLPaWAsWm7SLFO9yRmcPppd6mvyLQ0vntz83gBcTBF1fW71n4ka5-i8aAgleEALw_wcB&gclsrc=aw.ds) - Fill to yellow line, probably just needs to be topped off 1x per year. While checking this oil level, look at the air filter on the chiller and wash it with water if it's dusty.
- [Honing oil](https://www.mscdirect.com/product/details/00581108?cid=ppc-google-&mkwid=%7Cdc&pcrid=&rd=k&product_id=00581108&gad_source=1&gclid=Cj0KCQjwgJyyBhCGARIsAK8LVLMkqQYkdjLmiTbuxuM2LAm6sQW70pY0a4Z0ktqCmY1CGDyhzgZ0Jg0aAqiQEALw_wcB&gclsrc=aw.ds) - for honing the chuck and steel sample plates
- [Finishing oil](https://www.grainger.com/product/3-IN-ONE-Machine-Oil-Multipurpose-Oil-4UJ34) - for honing the chuck and steel sample plates

#### Sample preparation
- [Steel plate, 3x3"](https://www.mcmaster.com/1388K102/)
- [Steel plate, 3x6"](https://www.mcmaster.com/1388K106/)
- [Steel plate, 4x4"](https://www.mcmaster.com/1388K104/)
- [Mixing Cups](https://www.mcmaster.com/7632A21/) - Feel free to research a different option that works for you
- [Popsicle Mixing sticks](https://www.amazon.com/Mr-Popsicle-Sticks-Crafts-Crafting/dp/B08BBYHZ82/ref=sxts_b2b_ccp_search_w_op?content-id=amzn1.sym.df2081bd-b9c5-41f7-ae97-6c056112b3d5%3Aamzn1.sym.df2081bd-b9c5-41f7-ae97-6c056112b3d5&cv_ct_cx=popsicle%2Bsticks&dib=eyJ2IjoiMSJ9.pJWuzIyRl7_NMJgpavcV1x3Dlg6w2xd4hJ8NVAlNQpxnS5xRqoCt-C98lL04Qgl-H_H9W9ZR8rBvEm8UTyS716UuuG5_fGx708QUOHxc72P3VXvdGBuRl5fHdSFT1xdB.qN8XHprSsmn6eRcb2k3VxXUuAK2J0MAbI5D8F4MupBI&dib_tag=se&keywords=popsicle%2Bsticks&pd_rd_i=B08BBYHZ82&pd_rd_r=4bb49b04-5e58-40e8-816e-028c77efb771&pd_rd_w=gmSKm&pd_rd_wg=OrXB5&pf_rd_p=df2081bd-b9c5-41f7-ae97-6c056112b3d5&pf_rd_r=RK01J0E8SDFQ8PKG4T88&qid=1715975069&sbo=RZvfv%2F%2FHxDF%2BO5021pAnSA%3D%3D&sr=1-1-d27bdacb-ad14-3372-97fb-5f5070035007&th=1)
- [Structural Adhesive, High-Strength Epoxy, Devcon 14260, 1.69 oz. Cartridge](https://www.mcmaster.com/66215A24/)
- [Epoxy Structural Adhesive, Loctite 9460, 1.69 oz. Cartridge](https://www.mcmaster.com/1813A234/)

#### Coolant chemistry check
- [pH Test Strips](https://www.mcmaster.com/11235T62/)
- [Hardness Test Strips](https://www.mcmaster.com/11235T41/)
- [Alkalinity Test Strips](https://www.mcmaster.com/11235T51/)

#### Cleaning
- [Rags](https://www.mcmaster.com/7366T27/)
- [Paper Wipes](https://www.mcmaster.com/70585T1/)
- [Non-scratch Sponges](https://www.mcmaster.com/73055T25/)
- [Simple Green Cleaner/Degreaser Liquid](https://www.mcmaster.com/7428T12/)
- [Simple Green Cleaner/Degreaser Wipes](https://www.mcmaster.com/7360T17/)

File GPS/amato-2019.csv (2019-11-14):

Latitude | Longitude | HAE | MSL | ID | FeatureName | Comment | GNSS Height | Vert Prec | Horz Prec | Std Dev
39.107070315 | 16.795760095 | 291.987 | 251.945 | 1 | Point_generic | SE corner of SE cement block1145 | 251.945 | 0.1 | 0.1 | 0.000034
39.107050751 | 16.795707147 | 291.808 | 251.765 | 2 | Point_generic | sw corner of sw blk b4 bdg 1147 | 251.765 | 0.1 | 0.1 | 0.000044
39.105962563 | 16.796454623 | 290.662 | 250.632 | 3 | Point_generic | sw end concrt sw end brdg 1153 | 250.632 | 0.1 | 0.1 | 0.000034
39.107302633 | 16.796305323 | 291.396 | 251.359 | 4 | Point_generic | point 4 | 251.359 | 0.1 | 0.1 | 0.000018
39.107459757 | 16.797602712 | 282.629 | 242.606 | 5 | Point_generic | se corner rock by river 1212 | 242.606 | 0.5 | 0.4 | 0.000619
39.107620561 | 16.797526127 | 289.507 | 249.483 | 6 | Point_generic | red tin se side mid 1216 | 249.483 | 0.1 | 0.1 | 0.000047
39.107867538 | 16.797710281 | 296.908 | 256.885 | 7 | Point_generic | se rock wall 12:19 | 256.885 | 0.1 | 0.1 | 0.000032
39.108380611 | 16.797115079 | 327.124 | 287.091 | 8 | Point_generic | roadside corner cement blk 12:25 | 287.091 | 0.6 | 0.2 | 0.000060
39.108675470 | 16.797448950 | 335.485 | 295.455 | 9 | Point_generic | 12:28 ground by gate lock | 295.455 | 0.3 | 0.3 | 0.000111

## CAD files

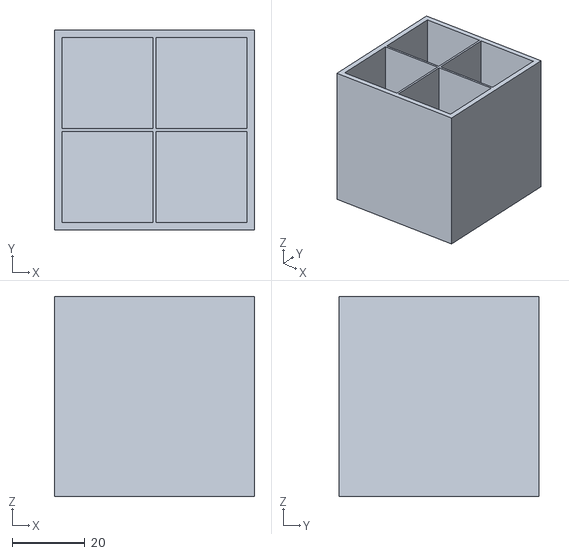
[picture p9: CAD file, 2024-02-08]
GIRI/cads_drawings/sample_embedding_boxes/ooids_box.stl
55.0 x 55.0 x 55.0

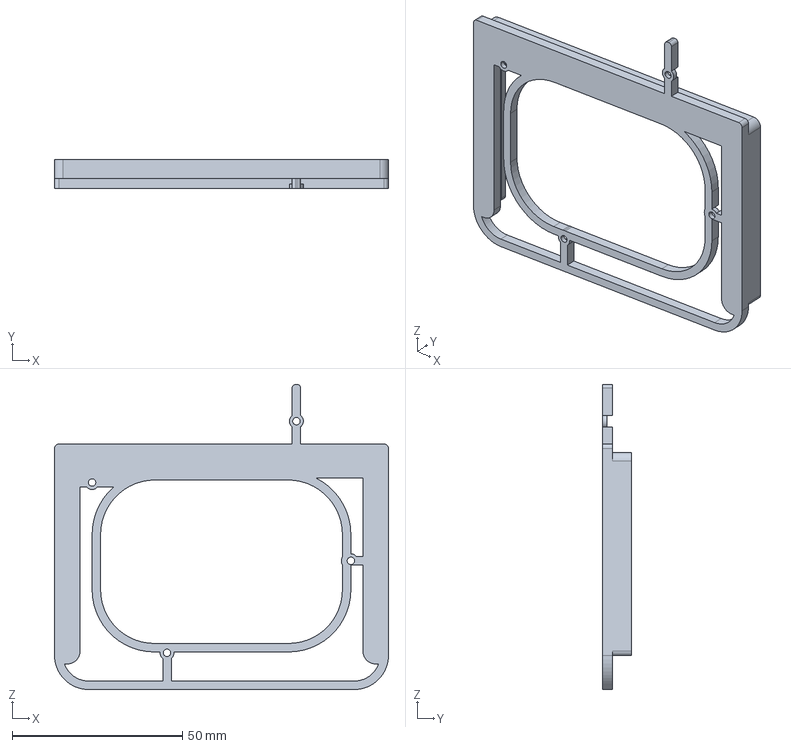
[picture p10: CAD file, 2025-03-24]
GIRI/cads_drawings/updatedFilterHolderv3.stp
98.1 x 8.59 x 89.6 mm

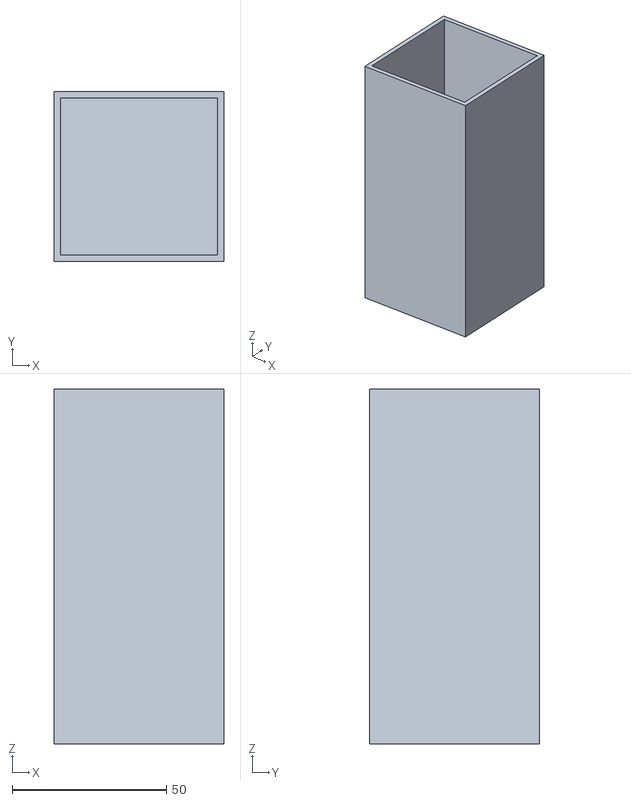
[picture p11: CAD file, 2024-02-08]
GIRI/cads_drawings/sample_embedding_boxes/epoxy_box.stl
55.0 x 55.0 x 115.0

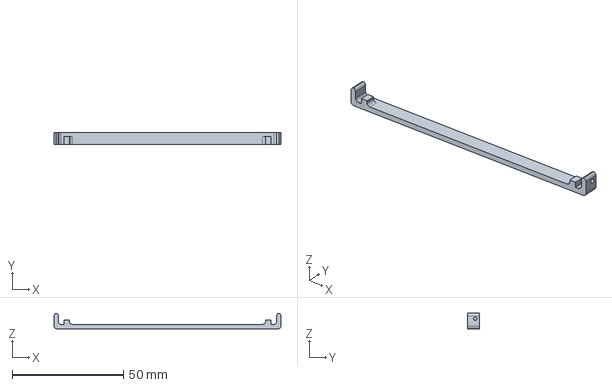
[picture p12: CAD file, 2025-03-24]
GIRI/cads_drawings/updatedTopElementv2.stp
102.1 x 5.59 x 6.97 mm

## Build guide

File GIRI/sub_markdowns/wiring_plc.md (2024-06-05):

## Wiring / electronics with PLC

#### Programable Logic Controller (PLC): 

To send signals between the grinder, control computer, and electronic peripherals, we use a programable logic controller (PLC). Our PLC is an Allen-Bradley Micro850 2080-L50E-48QVB. We chose a micro850 (L50E) unit as those are the current in-use units from Allen-Bradley. We previously had a Micro830, but those have since reached end-of-life. The 48QVB suffix in the part number refers to where we have to select the right model to fit our needs. A handy breakdown of different models can be found in [this guide](https://literature.rockwellautomation.com/idc/groups/literature/documents/sg/2080-sg001_-en-p.pdf), specifically on page 6. 48 refers to 48 inputs/outputs (28 inputs, 20 outputs), which we like to give us more room to expand peripherals. The QVB means the PLC takes 24V inputs and gives 24V *sinking* outputs. Note that most electronics do not take sinking outputs (also known as NPN), and instead require sourcing outputs (also known as PNP). We need the sinking output PLC model because that is what the grinder requires.  
  - [Manual for Micro800 controllers](https://literature.rockwellautomation.com/idc/groups/literature/documents/um/2080-um002_-en-e.pdf)

***A note on sourcing vs. sinking***: 
  - In general, sourcing and sinking is all about the direction of current flow in a DC circuit. For PLC systems, this concept describes the current flow relationship between digital PLC inputs/outputs and the input/output devices deployed in the field.
  - **Sourcing PLC input module**: In a sourcing system, the PLC provides the positive voltage to the field device, and the field device provides the path to ground. In other words, the PLC sources the current to the field device. 
  - **Sinking PLC input module**: In a sinking system, the PLC provides the path to ground, and the field device provides the positive voltage. In other words, the PLC sinks the current from the field device. 
  - **Sourcing PLC output module**: In a sourcing system, current will flow out of the PLC output module into the connected load. This is also known as **PNP** (positive-negative-positive) or N.O. (normally open) logic.
  - **Sinking PLC output module**: In a sinking system, current will flow from the connected load into the PLC output module. This is also known as **NPN** (negative-positive-negative) or N.C. (normally closed) logic.
  - **Sourcing PLCs are more common** because they are easier to wire and troubleshoot. However, some devices require sinking outputs, like the grinder.
  - For more information see this [website](https://www.dosupply.com/tech/2022/05/16/sinking-vs-sourcing-in-plcs/).

#### PLC modules and expansions: 
Because the PLC base is limited to digital inputs, and sinking digital outputs, we have several modules and expansions to allow for analog inputs/outputs, and sourcing digital outputs. Modules refer to rectangular blocks that install on top of PLC. Expansions install on the side of the PLC.
  - 2080-IF4 module: This module gives us up to four analog input channels. Currently, we use this module to get inputs from the temperature and humidity sensor.
  - 2080-OB4 module (x3): These modules give us four channels of sourcing outputs each. Because our PLC only has sinking outputs, we need these modules to send signals to most other electronics including: 
    - The ring light, which has 8 channels, and takes up two modules.
    - The grinding sensor (currently not in use).
  - 2085-OF4 expansion (x2): We have the option of controlling the brightness of each channel of the ring light by sending a 0-10V analog signal,10V being the brightest. These expansions give us the necessary 8 channels of analog voltage output. Currently, these modules are not in use, and the analog inputs to the ring light controllers are sent directly from the 24V power supply, leaving them at maximum brightness. If dimming control is wanted in the future, these modules could be used. That implementation would require new ladder logic.
  - 24 V power supplies: We have two 24V power supplies to power peripherals. The 1.6 amp unit directly attached to the PLC has enough current to send signals to the grinder, and power the PLC and temp/humidity sensor. As we added fancier lights, we needed more 24V current, so we have the 5 amp Eaton unit to provide reliable power to all LEDs.

#### Ring light:
We have a custom LED ring light built by Jeremy Broderson at Phi3 (~Jbrodersen@phi3.net~). Not much documentation was given with the light, but most information about controlling it can be found below with the [4ZMD controllers](https://smartvisionlights.com/wp-content/uploads/4ZMD_Datasheet.pdf). Included wavelengths in the light are: 470nm, 505nm, 530nm, 590nm, 625nm, 670nm, 740nm, and 940nm. The order in which they are controlled depends on the attachment of the 4ZMD, but they generally go in descending wavelength order. We currently have a hand-cut linear polarizing film from American Polarizers ([AP42-004T](https://www.apioptics.com/product/ap42-004t/)) placed between the lights and the diffuser window to help reduce specularity. Drawing for the ring light attached:
[Ring light full assembly](../cads_drawings/ring_light/FULL%20ASSEMBLY%205-19-2023.STEP)

#### 4ZMD Controllers: 
The ring light is controlled by two [4ZMD](https://smartvisionlights.com/products/4zmd/) devices from Smartvision (4 channels per controller). These devices allow us to control brightness through an analog input to each channel, and trigger the lights through PNP input lines. PNP means **these triggers require a sourcing output from the PLC**. Currently, We have the analog lines wired directly to our 24V power supply, so the brightness is not modulated, and they run at full brightness always. If brightness control were desired, the devices would have to be rewired to the 2085-OF4 expansions on the PLC and coded into the ladder logic.
  * Mini LED fix: We had some issues with the little indicator LEDs on the 4ZMDs not turning on even when a channel was successfully triggered and the rind light turned on. This issue likely relates to the PCB driver blades shifting during shipping or handling. The fix is easy and can be done with the unit installed. Simply disconnect power, remove the front face cover and use a plastic pen, not metal, to push the board socket contacts down so the blade seats in the socket.
    * [photo 1](../photos/4zmd_fix/4zmd1.jpg)
    * [photo 2](../photos/4zmd_fix/4zmd2.jpg)
    * [photo 3](../photos/4zmd_fix/4zmd3.jpg)

#### UV brick light:
#### air:
#### connections to grinder:
#### temperature/humidity sensor:

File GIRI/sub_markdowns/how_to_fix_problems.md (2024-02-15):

# Some problems we've encountered and how to fix them
Add to this if you have a problem.

1. Grind stops for no apparent reason
- Is the sample in imaging position or grinding position?
    - (GRIND coordinates should be 0 for grind position)
    - If it's in grind position (i.e. not under the camera), did it finish the grind? Did the grind get imaged yet? 
    - If it's in imaging position and the computer says it took photos, check the last set of photos. You can also count the number of sets of photos it did take and compare that to the number you expected.
    - run ```recover_grinding_slice``` just in case. Compare these new images to the last set the program took. Keep them if they're different, otherwise delete them. (Wet the sample before you take images.)
- Check the computer > PLC connection
    - If you were able to run ```recover_grinding_slice```, this connection is fine and probably was not the problem.
    - Try turning the lights on and off.
- Check the PLC > Grinder connection (if computer > PLC works)
    - manually try grinding or teaching or something. (I (Julia) am unclear about this process because this has always been the problem for me so far.)
- POWER CYCLE
    - Unplug the PLC and plug it back in
    - Restart the grinder software (control-alt-delete).
    - Try to start a grind again. Hopefully everything is okay.
**Example scenario:**
Grind stopped overnight. Last command was JOB START and it was sent and received, so grind 111 should have begun. Images from grind 110 were taken and the sample was still in imaging position. There were no yellow lights on the PLC, "START" was still yellow on the grinder computer. The computer to PLC connection was fine and I was able to ```recover_grinding_slice``` (deleted the photos).
**Solution**:
I restarted the software on the grinder computer, moved the table back to x=0 in grinding coordinates, changed the number of grinds, and pressed start. It is working. (I did not have to power cyle the PLC.)

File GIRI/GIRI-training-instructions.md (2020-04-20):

# Giri Training Instructions
Training has two phases. The first is making training data, second train a neural network 

### In Photoshop
1. Open Photoshop
2. Open image
3. Create new layer--one for each class
4. Using the magnet tool, trace an object then use the bucket tool to fill (try to stick with primary colors if possible)
5. When finished tracing, select the layer on the bottom right panel
and click on one of the traced elements from that layer with the
magic wand. Then delete the layer and fill it again with the same
color. This gets rid of the gradient at the edge of the image. (check
the anti-aliasing box on the top toolbar). Repeat for each layer.
6. If you are training half-size images, then click on Image --> Image Size --> decrease the height and width of the image by 50% 
7.  Go to Image --> Mode --> 8 bits/channel
8.  Select all layers except for the layer containing the original image (often labelled background). 
9.  Go to Image --> Mode --> Indexed Color. It will ask if you want to merge layers, select "OK"
10. Save as tif. Make sure the background is deleted and only the training mask is present.

### In MATLAB
- Use train_with_multiple.m script
- more to come on this section.

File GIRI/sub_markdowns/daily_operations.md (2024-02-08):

## Daily operations to grind and image a sample
1) Stick a ruler in the coolant tank to measure the depth. If there is less than 6” depth, the level is a little low and more should be added (see: Mixing and adding coolant).

2) If the wheel has not run in a few hours, allow it to run for 10 minutes or so to rebalance. You can continue to prep the run while the wheel is warming up. **Note: Glasses on while wheel is running**

3) Turn on the coolant and use a plastic pipette to draw some up from the spout and make a refractometry reading. It should read just above 2. In this case, as long as there aren’t long-term increases in refractometry, it’s okay.

   *Steps 4-6 do not need to be done daily. Maybe once a month*

4) Use a pH strip to check pH. Should be 9-10, higher is better.

5) Use a strip to check hardness. Should be around 250.

6) Use a strip to check alkalinity. Should be greater than 240.

7) Use a wet paper towel to wipe off the orange roller.

8) Check the black back curtain to make sure it won’t get pushed down by the roller during the run. Reposition if needed.

9) On the onboard computer, check the number of loops programmed in the G code (third line “M98P1000L___” with number of loops coming after L). If needed, change the number of loops to fit what you need for this run. No more than ~250 per run please.

10) On the onboard computer, push the big green ‘Start’ button.

11) Write measurements taken of coolant into the notebook log.

12) Check the amount of space on the hard drive to ensure there is enough room for the images to be taken during this set of grinds. 

13) Type the command barebones_serial into Matlab and follow the prompts to get the grind started.
   
### Mixing and adding Coolant

1) Depending on desired volume of coolant, pour DI into bucket. Usually 5 or 10 L

2) Add coolant at 2.5% concentration (always put DI in bucket and add coolant to it)

3) Stir

4) Pour into machine through the filter paper.

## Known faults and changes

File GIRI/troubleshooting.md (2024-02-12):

# Troubleshooting grinds
#### Shutter speeds and program wait times
There are a number of hardcoded wait times (and pauses) in the code. This means that if you increase shutter speeds beyond the length of the wait times, you may run into unexpected errors during your run. These crop up during the checking of thumbnail images and (likely) in verifying images. A great item for the to-do list would be to un-hard code these wait times, and instead use the longest shutter speed + a buffer. (Long shutter speeds are useful for UV -- I (Julia) have been using 20s, but I think 25s looks even better for a lot of images.)  

**Waiting times in the grind code**
1. ```verify_ims_exif``` line 42: ```pause(15);```
   - This pause comes after raw images have been captured (we see the message "Done with the image sequence, now generating thumbnails.") and before we generate thumbnails. Increasing pause time *might* mean that the program has to do fewer checks for images. It depends if the images have been completely captured by the time the pause comes, or if the command to capture has been sent but the images are not yet received. (I.e. if the longest shutter speed is 20s, the 15s pause would not be long enough to see that image come in.)
   - I have left the pause at 15 and things have been okay, even though my longest shutter speed is 20s.
2. ```image_capture``` line 15: ```[proceed, message] = wait_for_image(45);```
   - Here we *definitely* waiting for the image, and the time (45s) must be longer than the longest shutter speed.

**Issues verifying images**
There are some hard-coded thresholds that are used to check that image i+1 is sufficiently similar to image i, which is a proxy for everything working as planned. However, some rocks have enough variability at the 20 micron scale (i.e. the grinding interval) that I have found these thresholds to be *too restrictive*. Each time thresholds are not met, the grind stops, the user receives a text, and must come in to re-start the machine.  

If you have to re-start after receiving a text that says: "Please come in! ... Error message is: Images Not Verified." Here is what you should do:  

1. (Optional, but helpful): **Check which threshold / wavelength failed**
   - Manually run the parts of ```verify_ims_exif``` that check the thresholds:
     - line 137: set ```raw_listing``` to the path where your files are:
       - ```raw_listing = dir();```
     - also run line 140: ```[~,sorted_idx] = sort([raw_listing.datenum]);```
     - Highlight lines 149-169 (```comp_status = zeros(...)``` through the end of the ```for``` loop and run it in the command line. Once it runs, check the variable ```comp_status``` to see which image(s) triggered the threshold failure(s). (It will look like [1,0,0,1,1], which would mean that the 2nd and 3rd wavelengths triggered the failure.
        - Then you can just run the interior of the for loop for the image(s) that failed. Set ```i =``` whichever image you want to explore. Comment out line 169 (```comp_status(i) = thumbnail_comparison(...)```). Uncomment line 170 (```[x_status, x_simi,...] = thumbnail_comparison(...)```. Highlight the interior of the for loop and run it in the command line. Check the variables:
           - ```x_status```: 0 or 1 (fail, true)
           - ```x_simi```: structural similarity
           - ```x_exp_pct_diff```: exposure percent difference
           - ```x_top_mean```: top values of difference image
           - (you can look at all the details in ```thumbnail_comparison.m```)
         - If any of them are larger than the thresholds (input variables into ```thumbnail_comparison``` on line 169, this is why your grind failed).
         - Manually check your images! If somethign truly has failed, address that problem [not covered here].
         - If all the images look okay, just lower the thresholds and re-start your run [see below]
   - When you **re-start** your run, the grinder will still think that the run is happening. This is okay. You will re-run ```barebones_serial``` and start a "new" grind as usual. **HOWEVER** you will need to decrease the number of grinds to whatever the grinder computer thinks is happening (top of your script, number of times the loops are called) *minus* the number of grinds that have already happened. You can easily figure out how many have happened either by checking the output in the command window (the last line that says "Grind number X is under way.") or by looking at how many images have been taken (in finder, select all the photos from this grind and divide by the number of wavelengths). (So just tell the barebones_serial prompt that there are fewer grinds than the grinder thinks there are.)

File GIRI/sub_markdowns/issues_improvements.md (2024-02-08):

## Known current issues or improvements we would like to make
- [ ] Implement retry commands during imaging, checking for files, and making thumbnails. 

  *Entered: Thursday, October 26, 2023 at 11:44:28 AM*

- [ ] Identify machine restarts we can perform remotely by logging into the control Mac. 

  *Entered: Thursday, October 26, 2023 at 11:45:13 AM*

- [ ] Adjust timing for generating thumbnails so the retry doesn’t take so long. 

  *Entered: Wednesday, January 31, 2024 at 11:08:19AM*

- [ ] Test and implement flexible thresholds for image comparison. 

  *Entered: Wednesday, January 31, 2024 at 11:10:36AM*

- [ ] Function for easy checking of similarity metrics for previous 2 grinds

  *Entered: Thursday, February 8, 2024 at 6:35:46 PM*

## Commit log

2019-11-14 Added export instructions and included a test dataset and example
    [amato-2019.csv]
2019-11-18 sarahs sercon sample prep mardown document
2024-05-14 added lens and filter info with some figures
2025-03-24 plastic holder for Wood's glass filter
    [updatedFilterHolderv3.stp, updatedTopElementv2.stp]
